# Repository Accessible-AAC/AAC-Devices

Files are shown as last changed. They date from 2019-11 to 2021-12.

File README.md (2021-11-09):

# AAC-Devices

Augmentative and alternative communications device design files based on inexpensive and open source technologies.

Printed circuit boards were designed using KiCAD (https://www.kicad.org/)

Enclosures were designed using OpenSCAD version 2015.03-2 (https://www.openscad.org/).

Solutions are designed around commodity electronic devices that should be inexpensive and readily available on-line.

<br />
This work is licensed under a <a rel="license" href="http://creativecommons.org/licenses/by-sa/4.0/">
Creative Commons Attribution-ShareAlike 4.0 International License</a>.

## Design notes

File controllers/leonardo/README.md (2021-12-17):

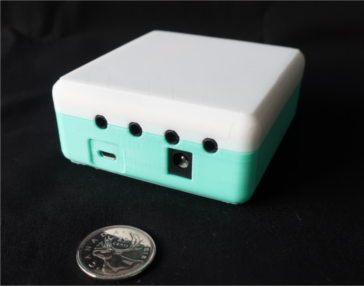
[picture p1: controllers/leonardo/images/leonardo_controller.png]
 

# Arduino Leonardo Controller

CAD files and firmware for a controller based on an Arduino leonardo board (https://store.arduino.cc/usa/leonardo) and a custom daughter board. 

## Leonardo Firmware

The most recent firmware for the controller can be found here: https://github.com/AbilitySpectrum/netCle/tree/master/Arduino/HubV1
(Please note that the firmware has been deprecated and is no longer actively supported.)

## Daughter Board Design Files

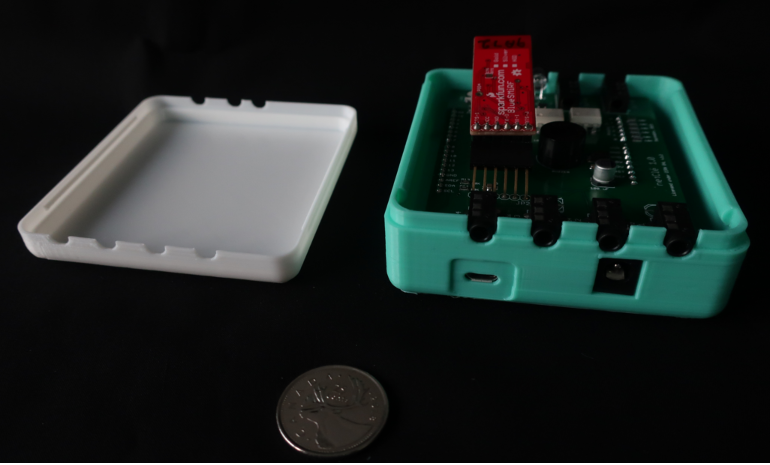
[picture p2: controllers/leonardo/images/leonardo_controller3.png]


The design for the daughter board can be found here: https://github.com/AbilitySpectrum/Sensact/tree/master/Board/v4.2

<br />This work is licensed under a <a rel="license" href="http://creativecommons.org/licenses/by-sa/4.0/">Creative Commons Attribution-ShareAlike 4.0 International License</a>.

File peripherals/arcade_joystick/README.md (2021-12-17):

# Arcade Joystick

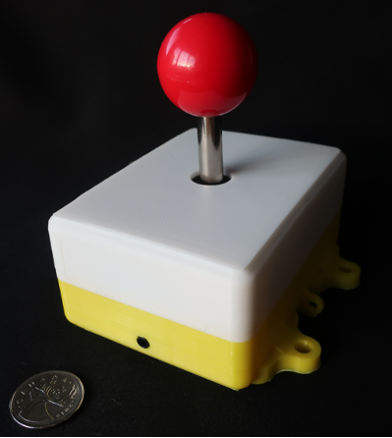
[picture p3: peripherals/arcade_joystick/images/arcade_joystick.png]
Arcade Joystick

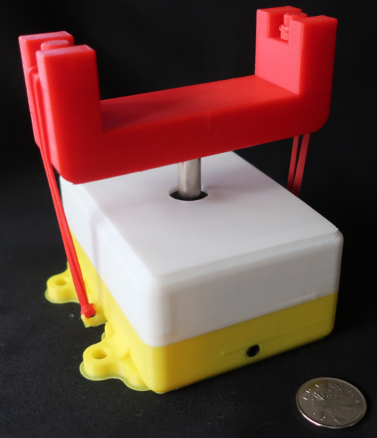
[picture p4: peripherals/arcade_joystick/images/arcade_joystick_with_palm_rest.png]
Arcade Joystick With Palm Rest


These directories contain design files for an arcade joystick peripheral.
 
This sensor can be plugged into an analog (yellow) controller input. It is activated by moving the handle.

## Assembly

Internal hardware mechanism is an arcade style 4/8 way joystick purchased from China.

It is held in place by four 8-32 x 1½" machine screws inserted into 4 embedded 8-32 nuts.

The joystick is connected to the interface PCB using hook-up wire:

    80 mm twisted pair soldered to D+, D-
    80 mm twisted pair soldered to R+, R-
    130 mm twisted pair soldered to L+, L-
    130 mm twisted pair soldered to U+, U-

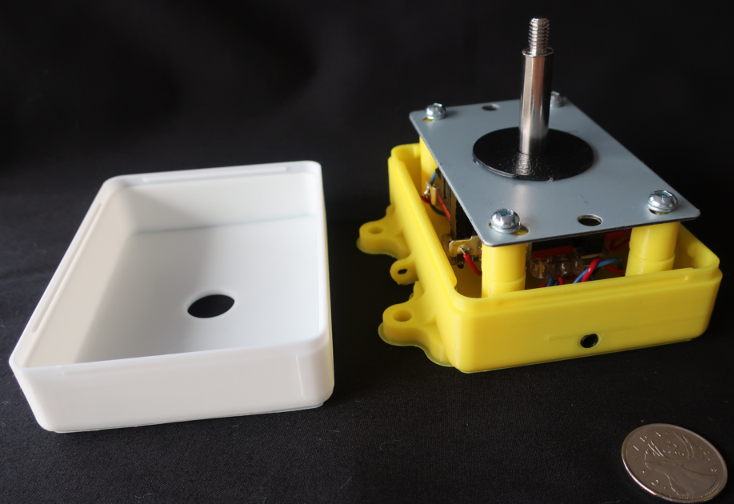
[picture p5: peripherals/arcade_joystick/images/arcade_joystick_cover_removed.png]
Arcade Joystick Enclosure with Cover removed


## Handles

The threads on the joystick handle are compatible with an M6 nut.

<a rel="license" href="http://creativecommons.org/licenses/by-sa/4.0/">

</a><br />This work is licensed under a <a rel="license" href="http://creativecommons.org/licenses/by-sa/4.0/">
Creative Commons Attribution-ShareAlike 4.0 International License</a>.

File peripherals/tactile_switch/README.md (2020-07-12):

# Tactile Switch

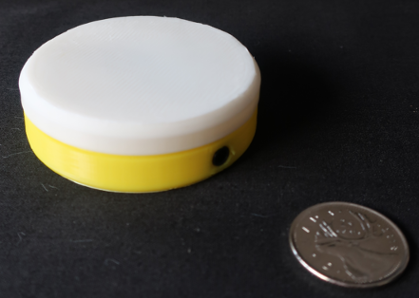
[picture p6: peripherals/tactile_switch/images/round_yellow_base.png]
Yellow Base Tactile Switch


These directories contain design files for a tactile switch peripheral.

When pressed, tactile switches with a yellow base connect the "Tip" on the TRRS connector to "Ring 1" and
can be connected directly into an analog (yellow) controller input. 

## Assembly

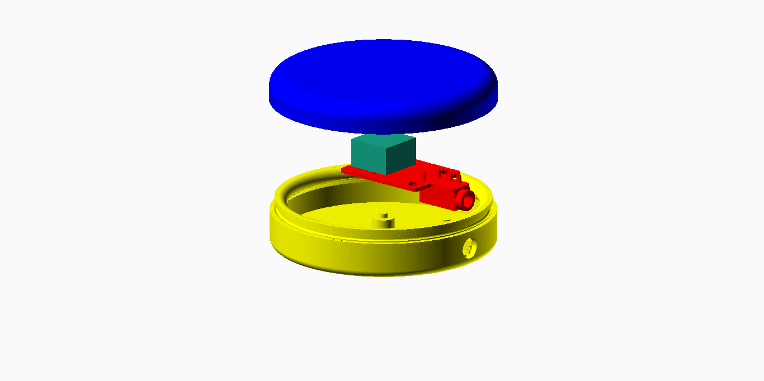
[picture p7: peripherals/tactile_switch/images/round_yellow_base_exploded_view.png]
Exploded View


## Parts

1 x 3.5mm Female Audio Connector 4 Pin DIP Stereo Headphone Jack PJ-320A

1 x 12mm x 12mm Tactile Switch

1 x tactile_switch_pcb_v2

1 x Round 59mm Button Enclosure

The PJ320A audio connector and the 12mm x 12mm tactile switch are available from various sources, including https://www.ebay.com/ and https://www.aliexpress.com/

<a rel="license" href="http://creativecommons.org/licenses/by-sa/4.0/">
</a>
<br />This work is licensed under a <a rel="license" href="http://creativecommons.org/licenses/by-sa/4.0/">
Creative Commons Attribution-ShareAlike 4.0 International License</a>.

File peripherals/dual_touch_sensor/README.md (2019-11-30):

# Dual Catalex Touch Sensor

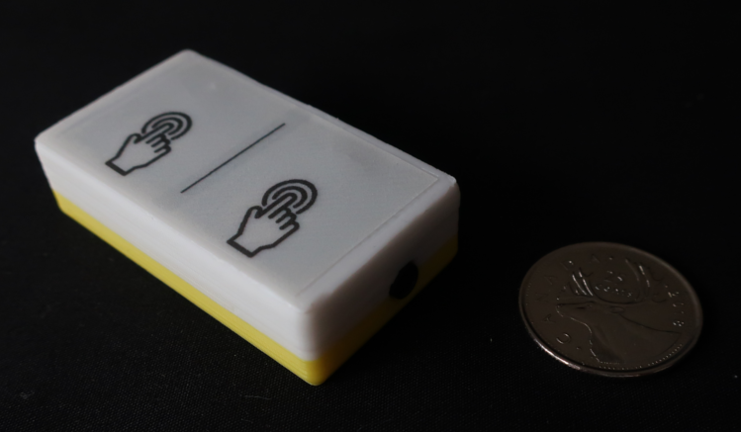
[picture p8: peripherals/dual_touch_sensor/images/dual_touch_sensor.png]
Dual Catalex Touch Sensor


These directories contain design files for a dual catalex touch sensor peripheral.

This sensor can be plugged into an analog (yellow) controller input. It is activated by touching the top, where indicated.

## Assembly

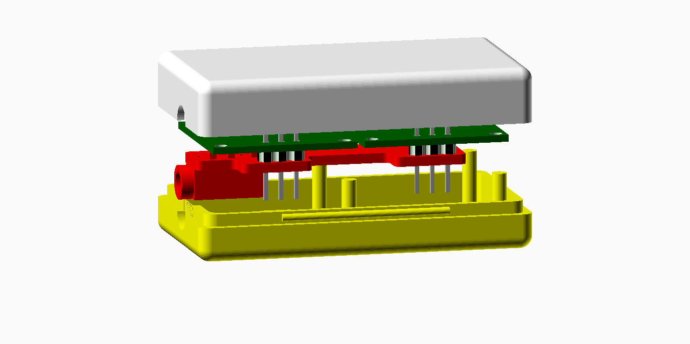
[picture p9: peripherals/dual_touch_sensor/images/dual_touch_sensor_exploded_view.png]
Exploded View


Catalex touch sensors should be tested before assembly to ensure that they will function correctly through the enclosure.

<a rel="license" href="http://creativecommons.org/licenses/by-sa/4.0/">

</a><br />This work is licensed under a <a rel="license" href="http://creativecommons.org/licenses/by-sa/4.0/">
Creative Commons Attribution-ShareAlike 4.0 International License</a>.

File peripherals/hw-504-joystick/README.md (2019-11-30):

# HW-504 Joystick

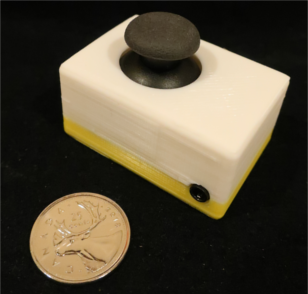
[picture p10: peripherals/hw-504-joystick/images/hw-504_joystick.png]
HW-504 Joystick


These directories contain design files for an HW-504 joystick peripheral.

This sensor can be plugged into an analog (yellow) controller input. It is activated by moving the black knob.

## Assembly

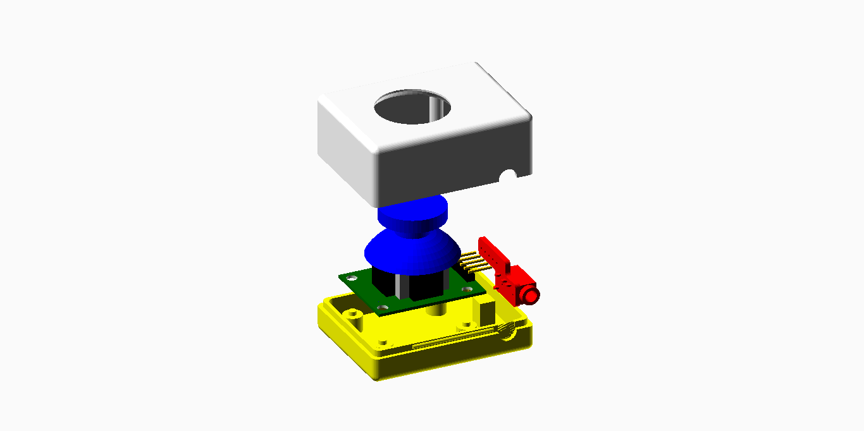
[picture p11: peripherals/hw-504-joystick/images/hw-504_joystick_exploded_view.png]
Exploded View


<a rel="license" href="http://creativecommons.org/licenses/by-sa/4.0/">

</a><br />This work is licensed under a <a rel="license" href="http://creativecommons.org/licenses/by-sa/4.0/">
Creative Commons Attribution-ShareAlike 4.0 International License</a>.

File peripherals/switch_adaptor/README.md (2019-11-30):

# Switch Adaptor

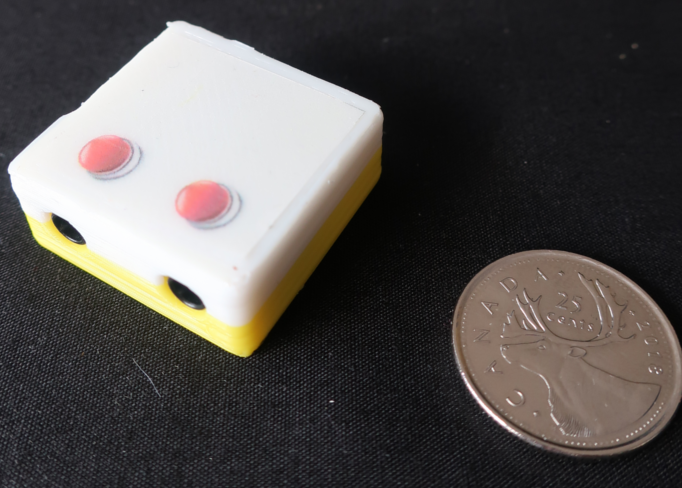
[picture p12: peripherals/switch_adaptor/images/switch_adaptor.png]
Switch Adaptor


These directories contain design files for a switch adaptor.

The switch adaptor is __required to connect a commercial switch (or a tactile switch
with a black base)__ to an analog (yellow) controller input. 

Switches should be plugged into the switch adaptor inputs indicated with the "red button icons".
The output connector (no icon) should be connected an analog (yellow) controller input.

__Failure to use a switch adaptor with these types of switches will result in the power being shorted
to the ground when the switch is pressed, possibly damaging the controller unit.__

## Assembly

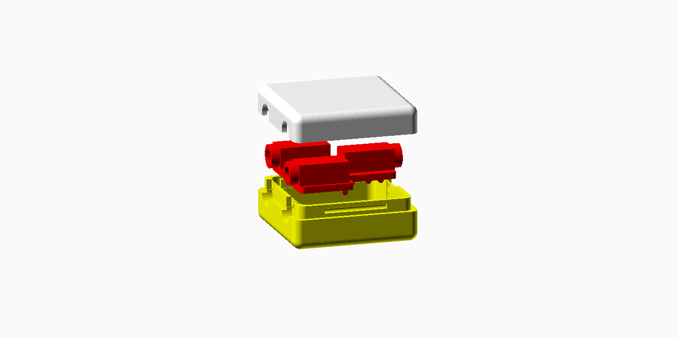
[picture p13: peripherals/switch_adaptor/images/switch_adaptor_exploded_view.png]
Exploded View


<a rel="license" href="http://creativecommons.org/licenses/by-sa/4.0/">
</a><br />
This work is licensed under a <a rel="license" href="http://creativecommons.org/licenses/by-sa/4.0/">
Creative Commons Attribution-ShareAlike 4.0 International License</a>.

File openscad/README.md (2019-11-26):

# OpenSCAD Common Files

The files in this directory are common files used to design various enclosures in this repository.

Files were created using OpenSCAD version 2015.03-2 (https://www.openscad.org/).

<br />This work is licensed under a <a rel="license" href="http://creativecommons.org/licenses/by-sa/4.0/">Creative Commons Attribution-ShareAlike 4.0 International License</a>.

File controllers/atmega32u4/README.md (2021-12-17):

# ATmega32U4 AAC Controller

These directories contain design files for two versions of an AAC controller based on the Atmel ATmega32U4.
The designs are functionally identical but use microcrontrollers in different form factors. 
Version 1.2 is based on an ATmega32U4-AU (44-TQFP) while version 1.3 is based on an ATmega32U4-MU (44-VQFNA).

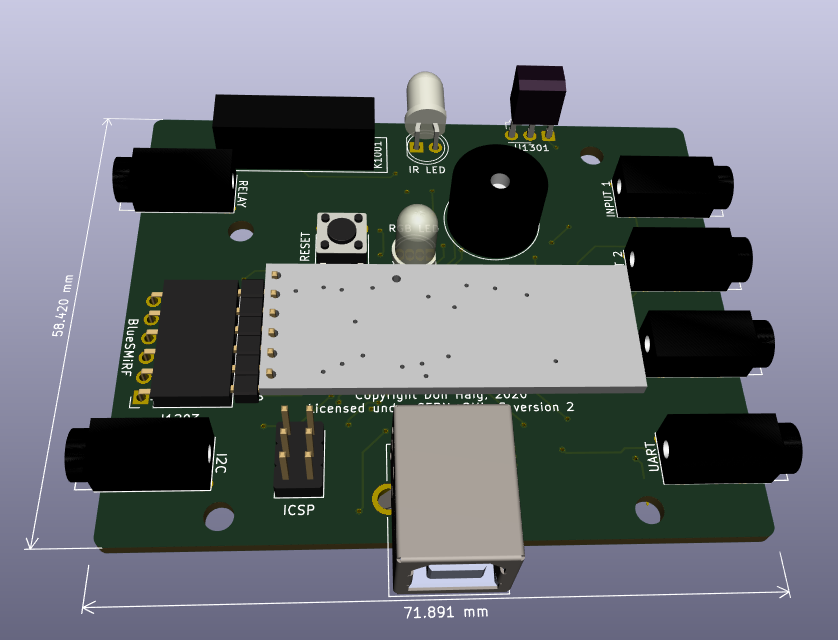
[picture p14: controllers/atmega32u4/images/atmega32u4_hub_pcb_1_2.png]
3D Rendering


## Firmware

The most recent firmware for the controller can be found here: https://github.com/AbilitySpectrum/netCle/tree/master/Arduino/HubV2

## netClé

This controller design is used in netClé™, distributed by the Tetra Society of North America: https://tetrasociety.org/netcle/

### Configuration 

Once programmed, the controller can be configured using: https://ncconfig.github.io/public_html/index.html

<br />This documentation is licensed under a <a rel="license" href="http://creativecommons.org/licenses/by-sa/4.0/">Creative Commons Attribution-ShareAlike 4.0 International License</a>.

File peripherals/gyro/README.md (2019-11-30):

# MPU-6050 Gyroscope/Accelerometer

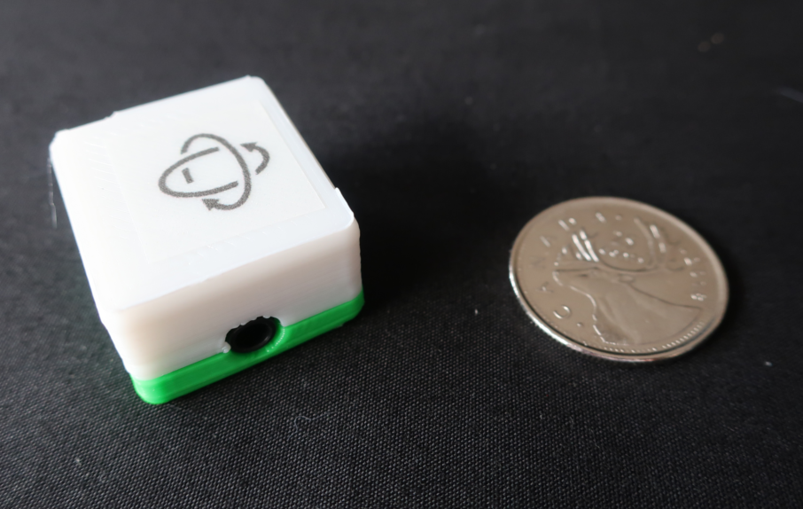
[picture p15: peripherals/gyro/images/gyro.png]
Gyroscope/Accelerometer


These directories contain design files for a gyroscope + accelerometer peripheral, for use with an
i2c (green) controller input.

## Hardware

The gyroscope/accelerometer peripheral is base on an MPU-6050 sensor:
<a rel="datasheet" href="https://www.invensense.com/wp-content/uploads/2015/02/MPU-6000-Datasheet1.pdf"> Datasheet</a>

I2C Address: 0x68

## Assembly

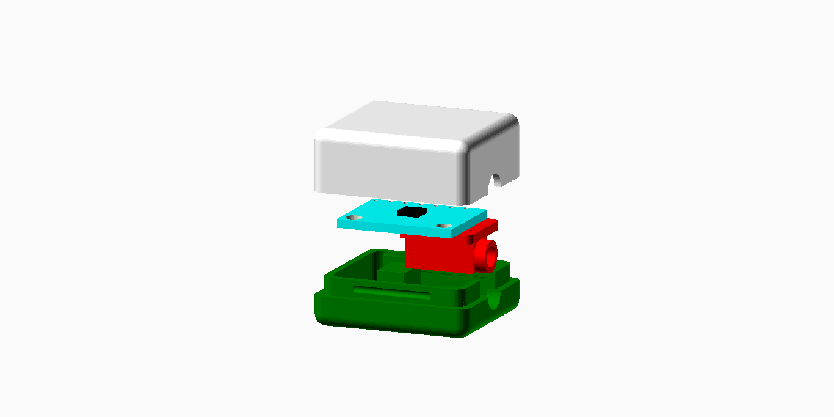
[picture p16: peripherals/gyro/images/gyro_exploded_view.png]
Exploded View


<a rel="license" href="http://creativecommons.org/licenses/by-sa/4.0/">

</a><br />This work is licensed under a <a rel="license" href="http://creativecommons.org/licenses/by-sa/4.0/">
Creative Commons Attribution-ShareAlike 4.0 International License</a>.

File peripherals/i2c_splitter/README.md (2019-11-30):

# I2C Splitter

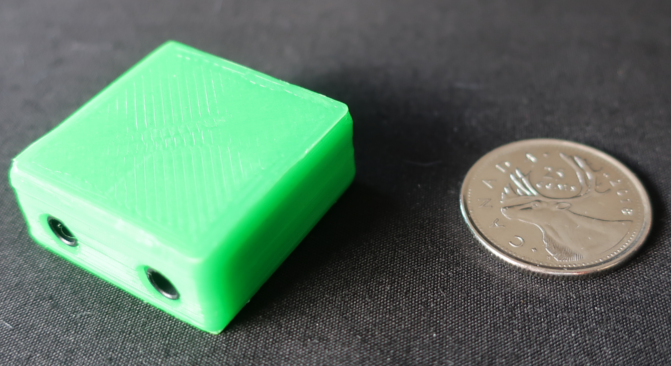
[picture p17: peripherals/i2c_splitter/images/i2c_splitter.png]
I2C Splitter


These directories contain design files for an i2c bus splitter, for use with an i2c (green) controller input.

This splitter can be used to connect two i2c (green base) peripherals to the same i2c (green) input port.

(Multiple splitters can be daisy-chained together to accommodate more i2c peripherals, subject to i2c bus limitation
with respect to peripheral addressing.)

## Assembly                                                                                                                                       

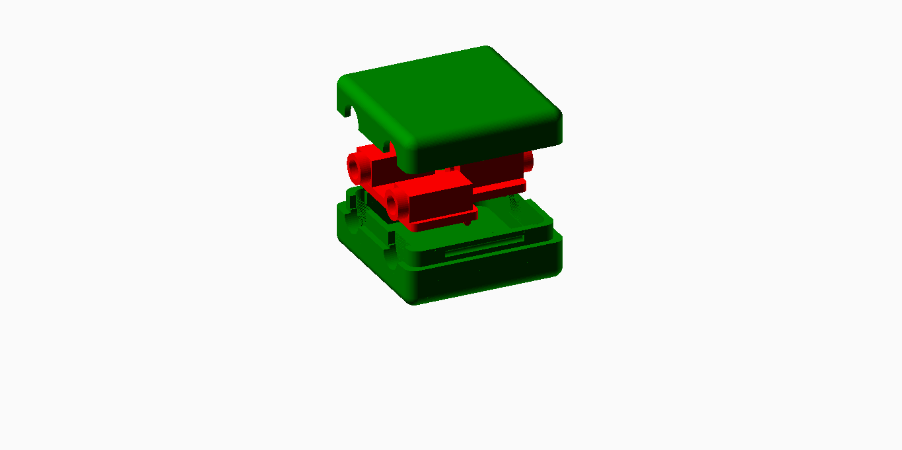
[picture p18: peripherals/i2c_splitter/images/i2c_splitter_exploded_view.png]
Exploded View
  

<a rel="license" href="http://creativecommons.org/licenses/by-sa/4.0/">

</a><br />This work is licensed under a <a rel="license" href="http://creativecommons.org/licenses/by-sa/4.0/">
Creative Commons Attribution-ShareAlike 4.0 International License</a>.

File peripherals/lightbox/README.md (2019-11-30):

# Lightbox Display

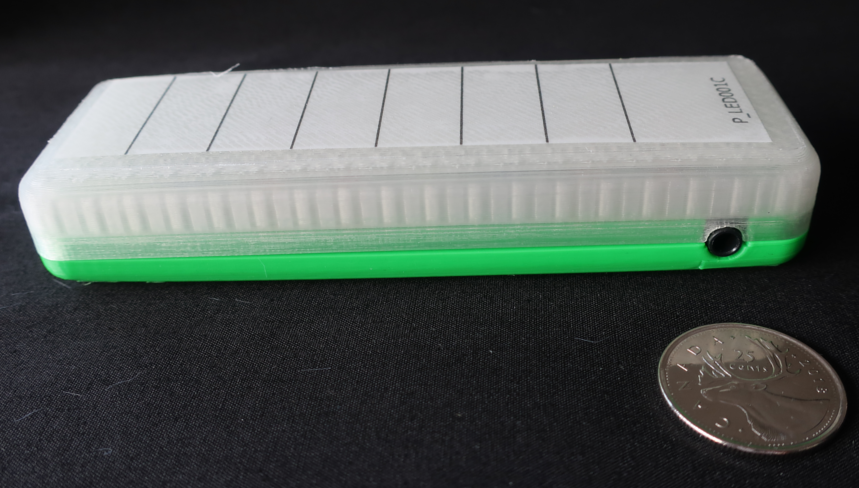
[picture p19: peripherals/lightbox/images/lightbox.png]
Lightbox Display


These directories contain design files for a lightbox display peripheral, for use with an i2c (green) controller input.

## Hardware

The lightbox is based on a Microchip MCP23008 8-Bit I/O Expander: <a rel="datasheet" 
href="https://ww1.microchip.com/downloads/en/DeviceDoc/21919e.pdf">Datasheet</a>

I2C Address: 0x20

## Assembly

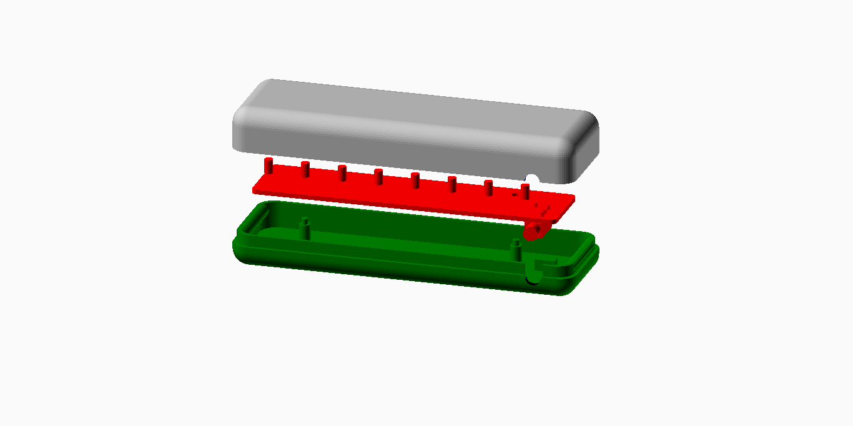
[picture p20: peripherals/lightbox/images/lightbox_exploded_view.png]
Exploded View


<a rel="license" href="http://creativecommons.org/licenses/by-sa/4.0/">

</a><br />This work is licensed under a <a rel="license" href="http://creativecommons.org/licenses/by-sa/4.0/">
Creative Commons Attribution-ShareAlike 4.0 International License</a>.

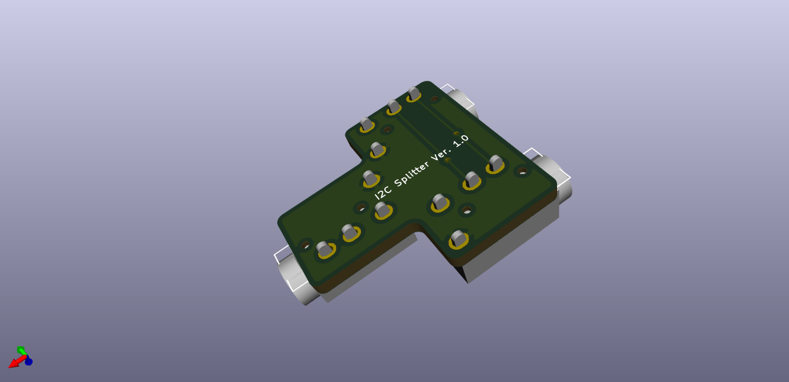
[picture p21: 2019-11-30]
peripherals/i2c_splitter/images/i2c_splitter_pcb.png

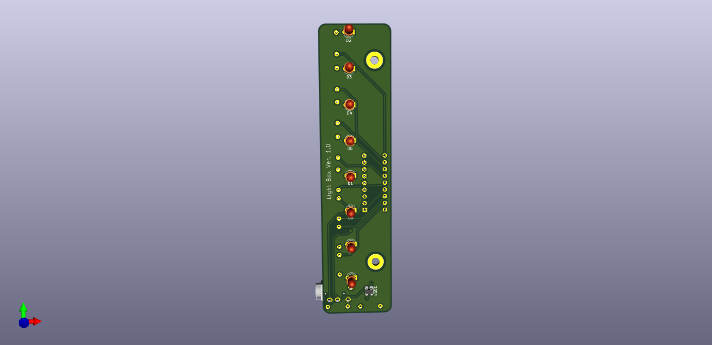
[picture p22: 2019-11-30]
peripherals/lightbox/images/lightbox_pcb_2.png

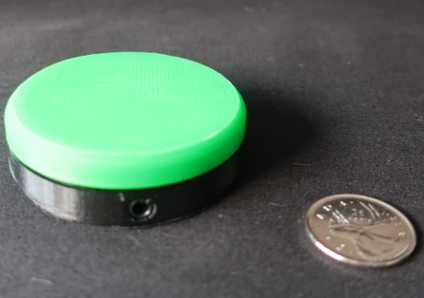
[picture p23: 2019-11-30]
peripherals/tactile_switch/images/round_black_base.png

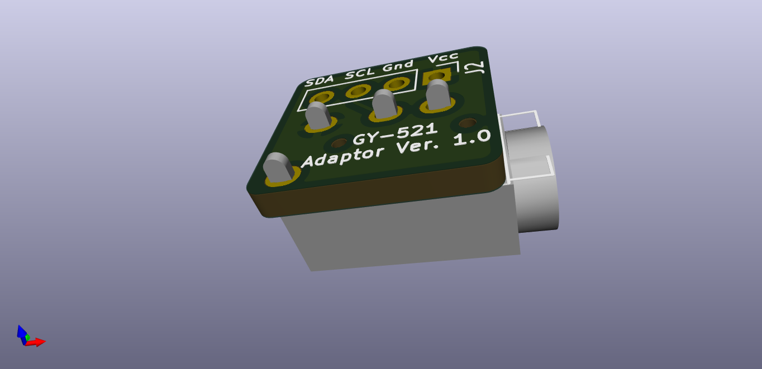
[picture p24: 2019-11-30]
peripherals/gyro/images/gy-521_trrs_pcb.png

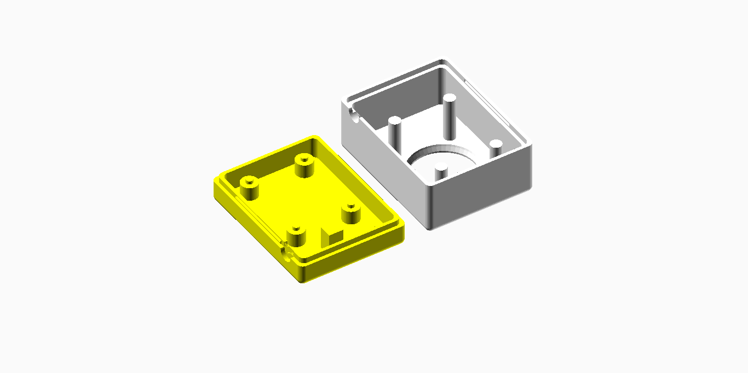
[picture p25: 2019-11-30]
peripherals/hw-504-joystick/images/hw-504_joystick_enclosure.png

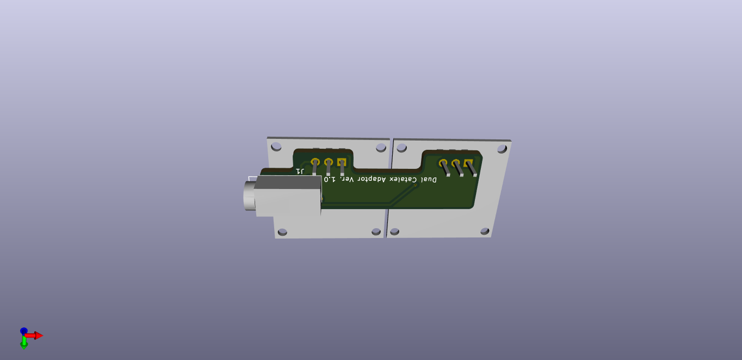
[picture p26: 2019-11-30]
peripherals/dual_touch_sensor/images/dual_touch_sensor_trrs_pcb.png

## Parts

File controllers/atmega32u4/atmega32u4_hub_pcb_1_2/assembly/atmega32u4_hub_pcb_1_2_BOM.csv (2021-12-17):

Comment | Designator | Footprint | LCSC
12mm_Buzzer | Buzzer701 |  |  | https://www.aliexpress.com/item/4000133619336.html?spm=a2g0s.9042311.0.0.27424c4dESjgPi
22uF | C101,C102,C103,C107,C108,C110,C111 | 805 | C45783 | https://lcsc.com/product-detail/Multilayer-Ceramic-Capacitors-MLCC-SMD-SMT_Samsung-Electro-Mechanics-CL21A226MAQNNNE_C45783.html
1uF | C104 | 805 | C28323 | https://lcsc.com/product-detail/Multilayer-Ceramic-Capacitors-MLCC-SMD-SMT_Samsung-Electro-Mechanics-CL21B105KBFNNNE_C28323.html
20pF | C105,C109 | 603 | C1648 | https://lcsc.com/product-detail/Multilayer-Ceramic-Capacitors-MLCC-SMD-SMT_Samsung-Electro-Mechanics-CL10C200JB8NNNC_C1648.html
100nF | C106 | 805 | C49678 | https://lcsc.com/product-detail/Multilayer-Ceramic-Capacitors-MLCC-SMD-SMT_YAGEO-CC0805KRX7R9BB104_C49678.html
10uF | C1101 | 805 | C15850 | https://lcsc.com/product-detail/Multilayer-Ceramic-Capacitors-MLCC-SMD-SMT_Samsung-Electro-Mechanics-CL21A106KAYNNNE_C15850.html
1N4007 | D1001 | SMA,DO-214AC | C95872 | https://lcsc.com/product-detail/Diodes-General-Purpose_MDD-Microdiode-Electronics-M7_C95872.html
RX | D101 | 603 | C72043 | https://lcsc.com/product-detail/Light-Emitting-Diodes-LED_Everlight-Elec-19-217-GHC-YR1S2-3T_C72043.html
RGB LED | D102 |  |  | https://www.aliexpress.com/item/1656753326.html?spm=a2g0s.9042311.0.0.27424c4dJetW7l
TX | D103 | 603 | C72044 | https://lcsc.com/product-detail/Light-Emitting-Diodes-LED_0603-Red-LED_C72044.html
L | D104 | 603 | C72038 | https://lcsc.com/product-detail/Light-Emitting-Diodes-LED_Everlight-Elec-19-213-Y2C-CQ2R2L-3T-CY_C72038.html
IR LED | D701
ESDA5V3L | ESD201,ESD301,ESD401,ESD501,ESD1101,ESD1201,ESD1202 | SOT-23-3 | C87911 | https://lcsc.com/product-detail/TVS_STMicroelectronics-ESDA5V3L_C87911.html
TLC-FSMD050 | F1201 | 603 | C261937 | https://lcsc.com/product-detail/PTC-Resettable-Fuses_TLC-Electronic-TLC-FSMD050_C261937.html
Conn_02x03_Odd_Even | J101 | PinHeader_2x03_P2.54mm_Vertical | C225518 | https://lcsc.com/product-detail/Pin-Header-Female-Header_CJT-Changjiang-Connectors-A2541WV-2x3P_C225518.html
USB_B | J1201 |  | C498173 | https://lcsc.com/product-detail/New-Arrivals_SOFNG-USB-B01_C498173.html
BlueSMiRF | J1203 |  | C225514 | https://lcsc.com/product-detail/Pin-Header-Female-Header_CJT-Changjiang-Connectors-A2541HWR-6P_C225514.html
PJ320A | J201,J301,J401,J501,J1001,J1202 |  |  | https://www.aliexpress.com/item/32775943831.html?spm=a2g0s.9042311.0.0.27424c4dvTAhw2
RELAY | K1001 |  | C10496 | https://lcsc.com/product-detail/Relays_PAN-CHANG-SIP-1A05_C10496.html
BSS138 | Q701,Q801,Q901 | SOT-23-3 | C82045 | https://lcsc.com/product-detail/MOSFET_ON-Semiconductor-BSS138LT1G_C82045.html
10k | R104,R101,R102,R103,R105,R108,R115,R116,R201,R202,R801,R802 | 603 | C25804 | https://lcsc.com/product-detail/Chip-Resistor-Surface-Mount_UNI-ROYAL-Uniroyal-Elec-0603WAF1002T5E_C25804.html
1k | R111,R113,R114 | 603 | C21190 | https://lcsc.com/product-detail/Chip-Resistor-Surface-Mount_UNI-ROYAL-Uniroyal-Elec-0603WAF1001T5E_C21190.html
330 | R112,R106,R107 | 603 | C23138 | https://lcsc.com/product-detail/Chip-Resistor-Surface-Mount_UNI-ROYAL-Uniroyal-Elec-0603WAF3300T5E_C23138.html
22 | R1202,R1201 | 603 | C23345 | https://lcsc.com/product-detail/Chip-Resistor-Surface-Mount_UNI-ROYAL-Uniroyal-Elec-0603WAF220JT5E_C23345.html
47 | R701 | 1206 | C25384 | https://lcsc.com/product-detail/Chip-Resistor-Surface-Mount_UNI-ROYAL-Uniroyal-Elec-1206W4J0470T5E_C25384.html
RESET | SW101 | 6mm x 6mm | C455095 | https://lcsc.com/product-detail/Tactile-Switches_XUNPU-TS-1002-07026_C455095.html
ATmega32U4-AU | U101 | QFP-44_10.0x10.0x0.8P | C44854 | https://lcsc.com/product-detail/ATMEL-AVR_ATMEL_ATMEGA32U4-AU_ATMEGA32U4-AU_C44854.html
TSOP38238 | U1301
16 MHz | Y101 | SMD-3225_4P | C13738 | https://lcsc.com/product-detail/SMD-Crystal-Resonators_Yangxing-Tech-X322516MLB4SI_C13738.html

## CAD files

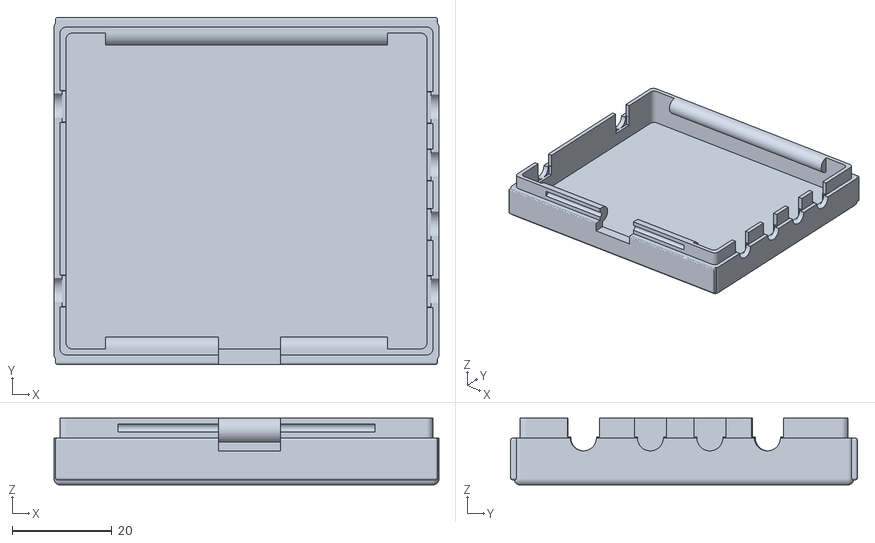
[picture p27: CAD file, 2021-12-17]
controllers/atmega32u4/enclosure/v1.2.2/stl_files/bottom.stl
77.0 x 69.4 x 13.4

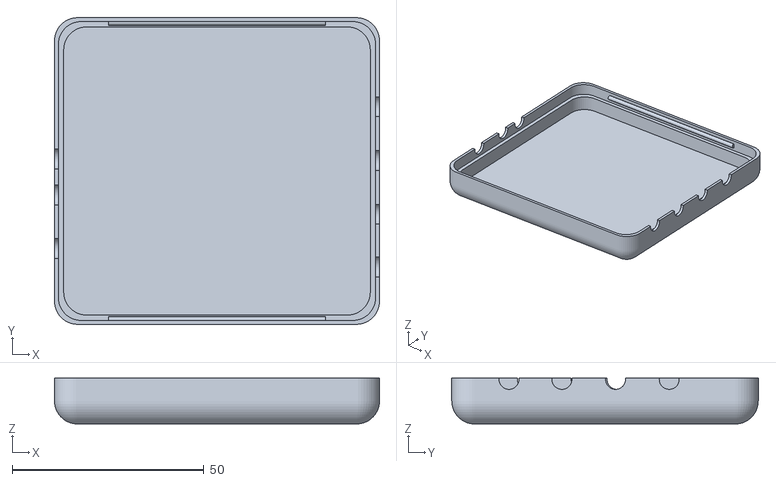
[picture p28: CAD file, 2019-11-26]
controllers/leonardo/enclosure/stl_files/v2/enclosure_top_v2.stl
84.8 x 80.0 x 12.0

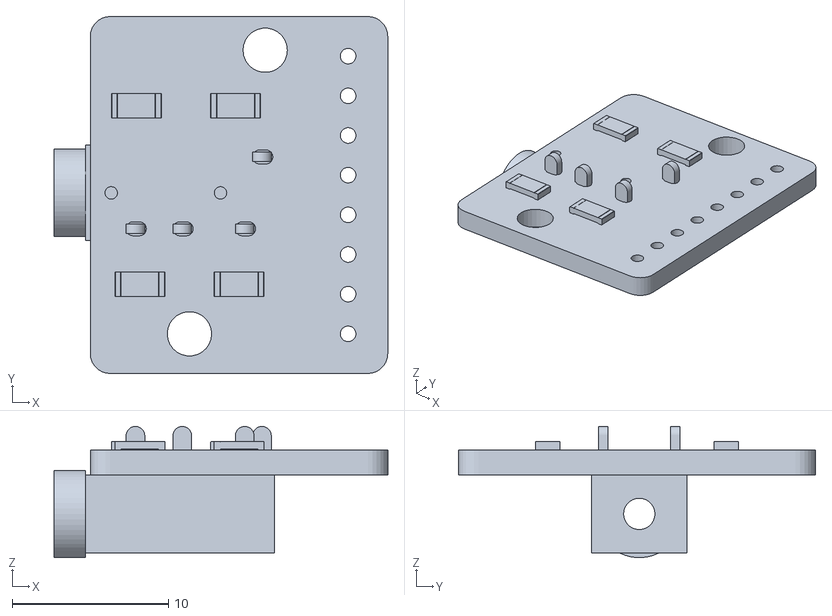
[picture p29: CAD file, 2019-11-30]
peripherals/arcade_joystick/enclosure/v3/interface_pcb.stl
21.4 x 22.9 x 8.39

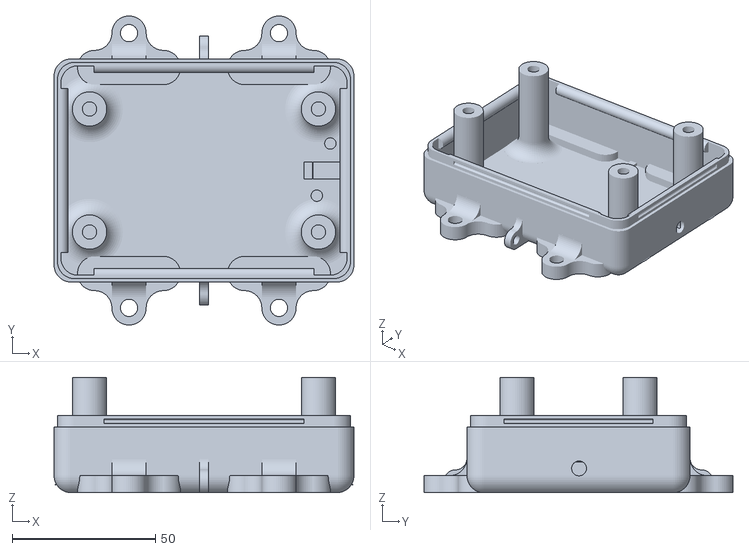
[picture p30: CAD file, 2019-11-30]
peripherals/arcade_joystick/enclosure/v3/stl_files/arcade_joystick_bottom.stl
104.8 x 108.0 x 40.4

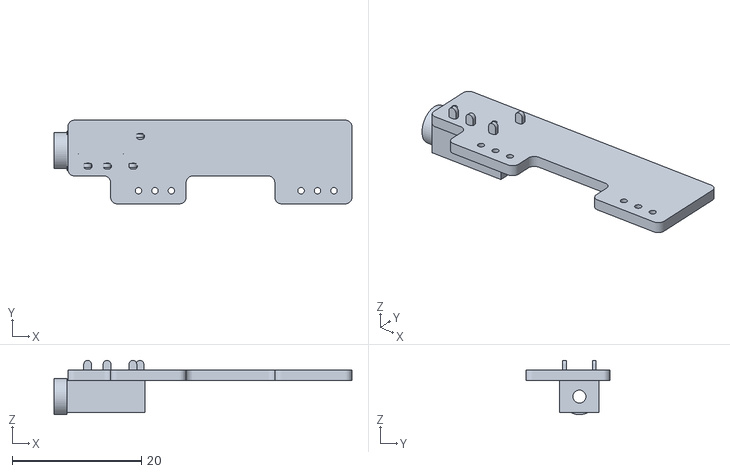
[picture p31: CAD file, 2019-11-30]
peripherals/dual_touch_sensor/enclosure/v2/dual_touch_sensor_pcb.stl
46.1 x 13.0 x 8.39

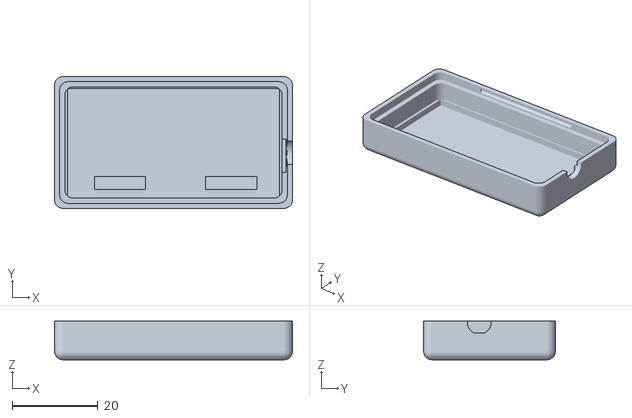
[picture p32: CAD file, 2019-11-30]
peripherals/dual_touch_sensor/enclosure/v2/stl_files/dual_touch_sensor_enclosure_top.stl
55.6 x 30.8 x 9.00

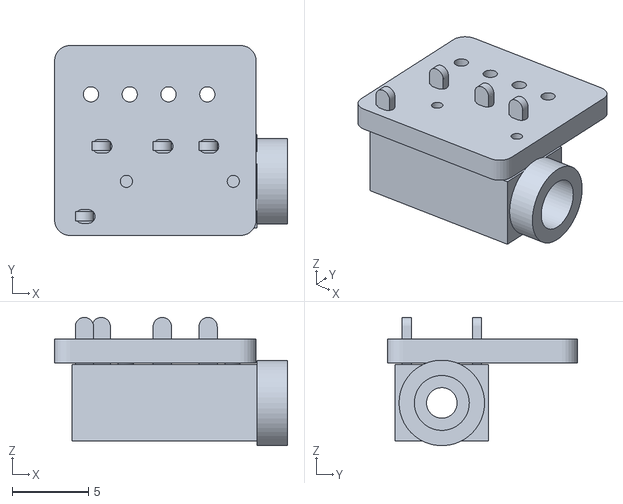
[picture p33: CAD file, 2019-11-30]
peripherals/gyro/enclosure/v2/gy-521_pcb.stl
15.3 x 12.4 x 8.39

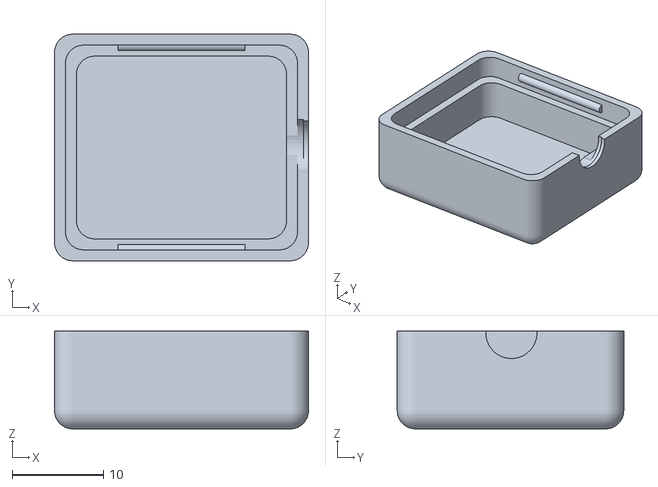
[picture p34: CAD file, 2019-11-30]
peripherals/gyro/enclosure/v2/stl_files/gy-521_sensor_enclosure_top.stl
27.8 x 24.8 x 10.7

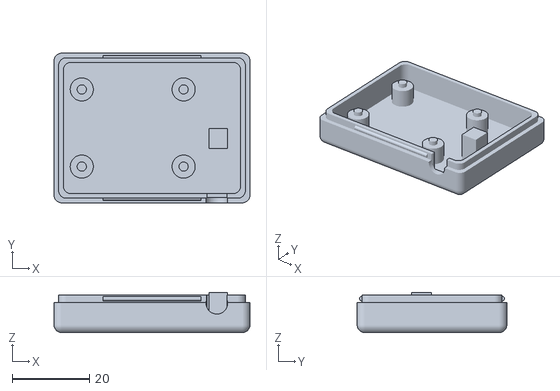
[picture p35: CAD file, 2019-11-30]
peripherals/hw-504-joystick/enclosure/v2/stl_files/joystick_enclosure_bottom.stl
50.8 x 38.8 x 10.4

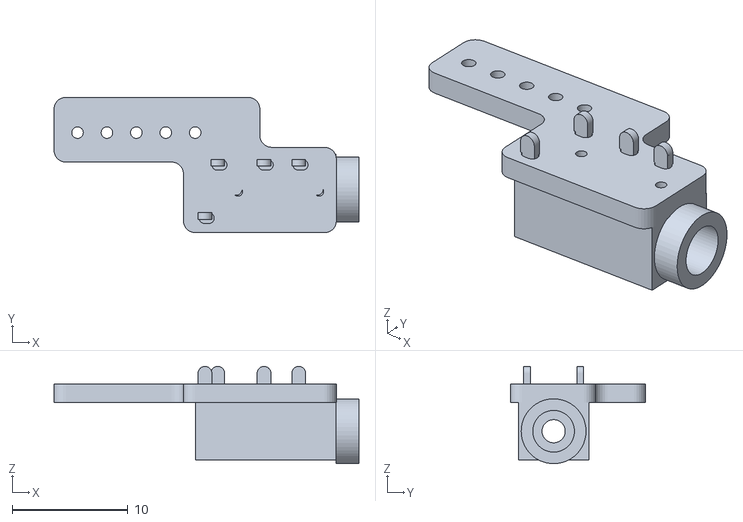
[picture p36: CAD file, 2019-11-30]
peripherals/hw-504-joystick/enclosure/v2/trrs_pcb.stl
26.3 x 11.7 x 8.39

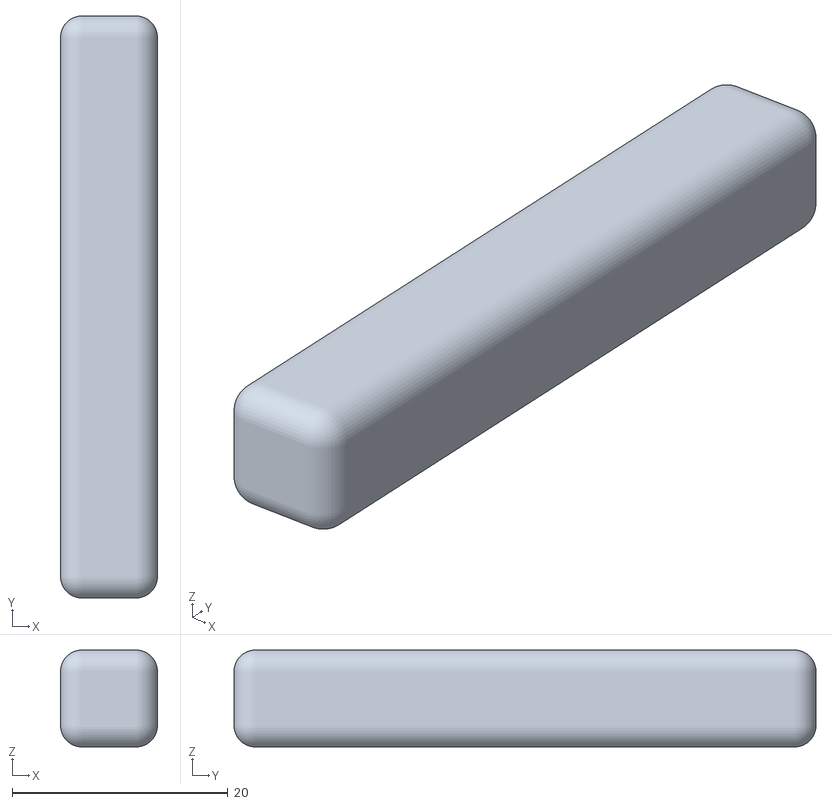
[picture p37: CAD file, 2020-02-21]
peripherals/hw-504-joystick/handle/stl_files/hw-504_handle.stl
9.00 x 54.0 x 8.99

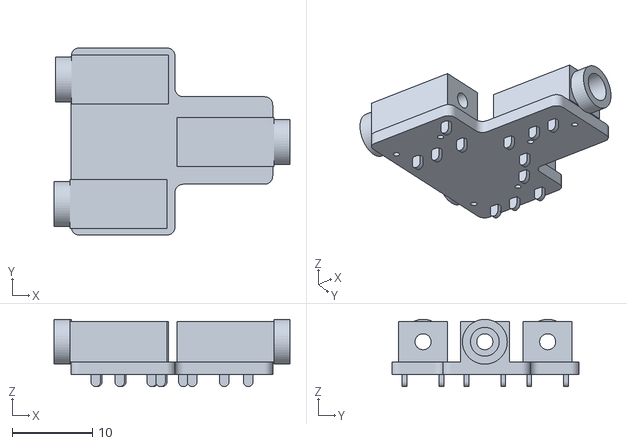
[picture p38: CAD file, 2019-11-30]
peripherals/i2c_splitter/enclosure/i2c_splitter_pcb.stl
29.4 x 23.4 x 8.39

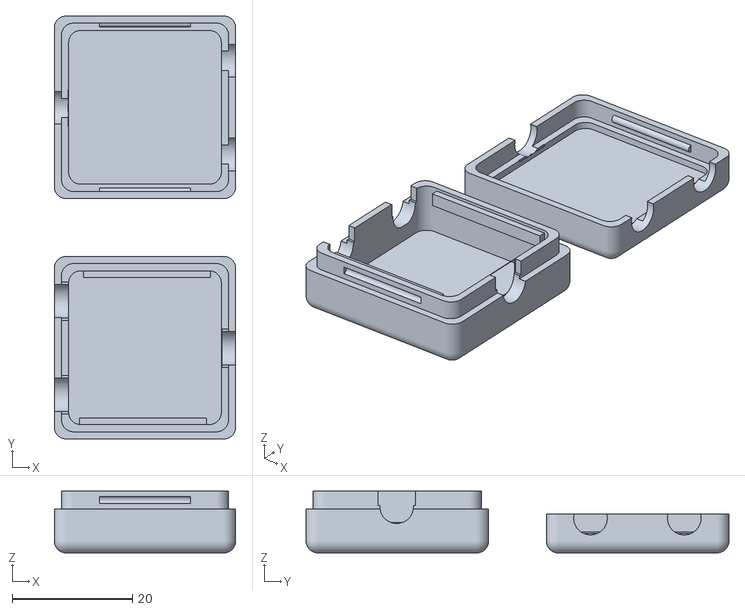
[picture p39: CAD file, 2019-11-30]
peripherals/i2c_splitter/enclosure/stl_files/switch_adaptor_enclosure.stl
30.2 x 70.4 x 10.3

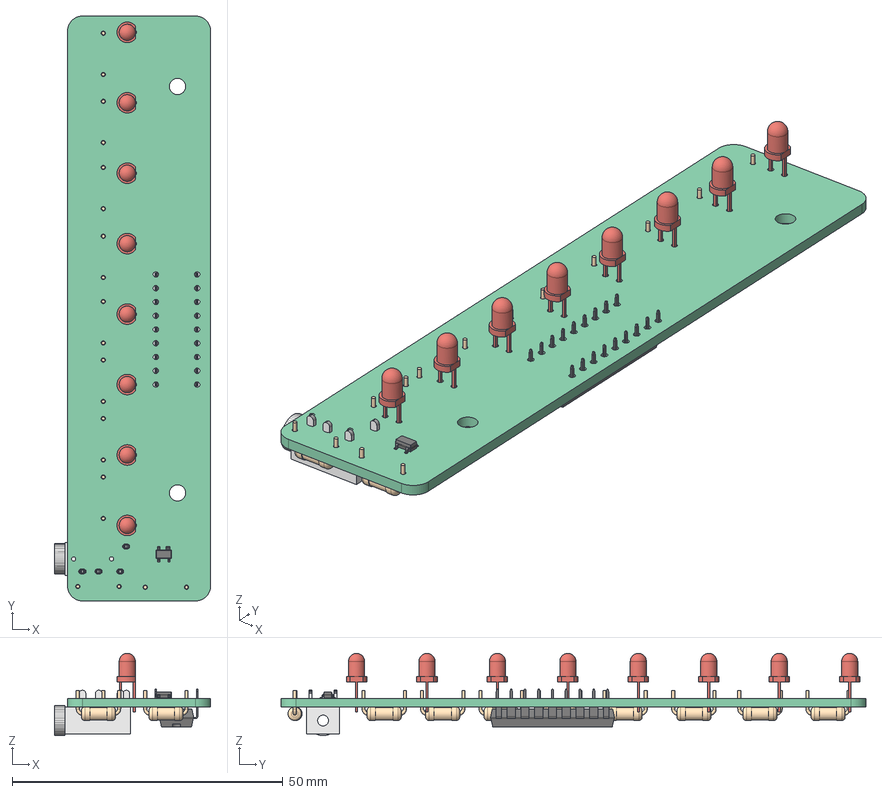
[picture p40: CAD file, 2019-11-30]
peripherals/lightbox/enclosure/v3/lightbox_pcb_v3.FCStd
28.8 x 108.0 x 15.2 mm
Pcb
ESD1_SOT_143_5CF6B7F7
D8_LED_D3.0mm_5CF71A60
D7_LED_D3.0mm_5CF6479C
D6_LED_D3.0mm_5CF647D2
D5_LED_D3.0mm_5CF64808
D4_LED_D3.0mm_5CF646B8
D3_LED_D3.0mm_5CF646EE
D2_LED_D3.0mm_5CF71B3B
D1_LED_D3.0mm_5CF64874
U1_DIP-18_W7.62mm_5CF635C0
R10_R_Axial_DIN0207_L63mm_D25mm_P762mm_Horizontal_5CF72305
R9_R_Axial_DIN0207_L63mm_D25mm_P762mm_Horizontal_5CF6BF18
R8_R_Axial_DIN0207_L63mm_D25mm_P762mm_Horizontal_5CF71A1C
R7_R_Axial_DIN0207_L63mm_D25mm_P762mm_Horizontal_5CF644EE
R6_R_Axial_DIN0207_L63mm_D25mm_P762mm_Horizontal_5CF64530
R5_R_Axial_DIN0207_L63mm_D25mm_P762mm_Horizontal_5CF645B4
R4_R_Axial_DIN0207_L63mm_D25mm_P762mm_Horizontal_5CF645F6
R3_R_Axial_DIN0207_L63mm_D25mm_P762mm_Horizontal_5CF64638
R2_R_Axial_DIN0207_L63mm_D25mm_P762mm_Horizontal_5CF71AFD
R1_R_Axial_DIN0207_L63mm_D25mm_P762mm_Horizontal_5CF70D55
J1_connector_pj320a002_(Solid)_5CF722CF[2]

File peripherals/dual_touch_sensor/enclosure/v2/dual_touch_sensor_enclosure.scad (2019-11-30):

/* dual_touch_sensor_enclosure.scad
 *
 *    OpenSCAD script to generate an enclosure for dual catalex touch sensor board
 *
 *    Copyright 2018 Don Haig (time4tux at gmail dot com)
 *
 *    GNU GPLv3 (See LICENSE for details) 
 *
 */
$fn = 50;

use<catalex_pcb.scad>
use<pj320a.scad>
use<rounded_minkowski_box.scad>
use<straight_header.scad>

u_d_pcb = 1.9;  // up - down adjustment on z-axis for PCB


/* 3D printer parameters */                                                                                                                      
    nozzle_diam = 0.4;    // 3D printer nozzle diameter in mm                                                                                         
    layer_res = 0.1;      // 3D printer layer resolution in mm                                                                                              

/* Enclosure Dimensions */
    tol = 0.01;                // printing tolerance (should be evenly divisible by nozzle diameter)
    lip_w1 = 1.2;              // thickness of outer lip (should be evenly divisible by nozzle diameter)
    lip_w2 = 1.2;              // thickness of inner lip (should be evenly divisible by nozzle diameter)
    t = lip_w1+lip_w2;         // total wall thickness (should be evenly divisible by nozzle diameter)
    l = 50.8+2*t;              // Outside Length of enclosure (should be evenly divisible by nozzle diameter)
    w = 26 + 2*t;              // Outside width of enclosure (should be evenly divisible by nozzle diameter)
    h_t = 8.0;                   // height of top piece of enclosure (should be evenly divisible by layer resolution)
    h_b = 6.8;                  // height of bottom piece of enclosure (should be evenly divisible by layer resolution)
    r = 2;                     // Outside corner radius
    lip_h = 2;               // height of lip (should be evenly divisible by layer resolution)


    check_dimension(l, nozzle_diam);
    check_dimension(w, nozzle_diam);
    check_dimension(t, nozzle_diam);
    check_dimension(lip_w1, nozzle_diam);
    check_dimension(lip_w2, nozzle_diam);

    check_dimension(h_t, layer_res);
    check_dimension(h_b, layer_res);
    check_dimension(lip_h, layer_res);

module connector(cutout) {

      translate([26.5, 2.4, 6.1])
     rotate([0,180,90]) color("black") pj320a(cutout);
}

module cover () {
    l = 22.0;
    w = 22.0;
    h = 0.3;

    difference() {
        minkowski() {
            color("white") cube([l, w, h], center=true);
            cylinder(r=2, h=h, center = true);
        }

    //translate([0, 0, h/2]) substrate();
    translate([0, 0, -1]) header_pins_cutout();
    //translate([-15, -15, -3.5]) cube([30, 30, 4.5]);
    }
}

module top() {
    module cut_out() {
        l = 48.8;
        w = 24.8;
        h = 1.8;

        translate ([0, -3, 12])
        difference() {
            minkowski() {
                color("white") cube([l, w, h], center=true);
                cylinder(r=0.4, h=h, center = true);
            }
        }
    }

    difference() {
        translate([0, 0, h_t+2])
        rotate([0, 180, 0])
        rounded_minkowski_outer_lip(l, w, h_t, r, lip_w2, lip_h, t, tol);
        connector();
        // pcb cut-outs
        translate([12.8+11.5, -0.8, 0]) cube([2, 7.8, 8]); // side
        translate([-4+11.5, +8, 9.6]) cube([12, 3, 2.2]);  // top
        translate([-4-14.5, +8, 9.6]) cube([12, 3, 2.2]);  // top
        //cut_out();
        //translate([11.5, 0, -t]) guts();
        translate([0, 3.2, -2.2]) color("red")cut_out();
    }
//    translate([0, 0, -t]) guts();

}

module bottom() {
    difference() {
        rounded_minkowski_inner_lip(l, w, h_b, r, lip_w1, lip_h, t, tol);
        connector(cutout = "down");
        //translate([8, 8, 3.2]) rotate([0,90,90]) color("black") pj320a(cutout = true);
        //magnets();
    }
   // connector backstop
   //connector(cutout = "down");
   translate([-2.4+11.5, 0, 0]) cube([5, 7, 3]);

   // Sensor supports
   s_c = 10.2;  // support center
   s_h = 9.5;
   //translate([s_c,s_c, 0]) cylinder(r= 0.8, h=s_h+1);
   //translate([s_c,s_c, 0]) cylinder(r= 2.5, h=s_h);

   //translate([s_c,-s_c, 0]) cylinder(r= 0.8, h=s_h+1);
   //translate([s_c,-s_c, 0]) cylinder(r= 2.5, h=s_h);

   //translate([-s_c,s_c, 0]) cylinder(r= 0.8, h=s_h+1);
   translate([-s_c+12, s_c, 0]) cylinder(r= 1.2, h=s_h);
   translate([-s_c-13, s_c, 0]) cylinder(r= 1.2, h=s_h);

   //translate([-s_c,-s_c, 0]) cylinder(r= 0.8, h=s_h+1);
   translate([-s_c+12,-s_c, 0]) cylinder(r= 1.2, h=s_h);
   translate([-s_c-13,-s_c, 0]) cylinder(r= 1.2, h=s_h);
}

echo(str("Rounded Minkowski Box: ", l, "mm x ", w, "mm x ", h_t + h_b, "mm") );

module guts() {
    translate([1.35, 0.2, 9.5+t]) touch_sensor_pcb();
    translate([-23.8, 0.2, 9.5+t]) touch_sensor_pcb();
    translate([-11.8, -5.8, 7.5+t]) rotate([0, 0, 180]) color ("red") import("dual_touch_sensor_pcb.stl");
}

module enclosure () {
    //translate([0, 40, h_t+2*t]) rotate([0, 180, 180])
    translate([0, 0, 15])
    color("white")top();

    //translate([-40, 0, -0.9])
    //translate([0, 0, 11])
    //rotate([0, 180, 0])
    //cover();

    //translate([0, 0, t])
    color("yellow")bottom();

    translate([11.5, 0, 3])
    guts();

}

//difference() {
enclosure();
//translate([5, 5, 0]) cube([50, 50, 50]);
//}

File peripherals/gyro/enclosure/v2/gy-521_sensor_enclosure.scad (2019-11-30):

/* gy-521_sensor_enclosure.scad
 *
 *    OpenSCAD script to generate an enclosure for mpu-6050 accel/gyro sensor board
 *
 *    Copyright 2019 Don Haig (time4tux at gmail dot com)
 *
 *    GNU GPLv3 (See LICENSE for details) 
 *
 */
$fn = 50;

use<mpu-6050_pcb.scad>
use<pj320a.scad>
use<rounded_minkowski_box.scad>
use<straight_header.scad>

u_d_pcb = 1.9;  // up - down adjustment on z-axis for PCB


/* 3D printer parameters */                                                                                                                      
    nozzle_diam = 0.4;    // 3D printer nozzle diameter in mm                                                                                         
    layer_res = 0.1;      // 3D printer layer resolution in mm                                                                                              

/* Enclosure Dimensions */
    tol = 0.01;                // printing tolerance (should be evenly divisible by nozzle diameter)
    lip_w1 = 1.2;              // thickness of outer lip (should be evenly divisible by nozzle diameter)
    lip_w2 = 1.2;              // thickness of inner lip (should be evenly divisible by nozzle diameter)
    t = lip_w1+lip_w2;         // total wall thickness (should be evenly divisible by nozzle diameter)
    l = 23+2*t;              // Outside Length of enclosure (should be evenly divisible by nozzle diameter)
    w = 20 + 2*t;              // Outside width of enclosure (should be evenly divisible by nozzle diameter)
    h_t = 9.2;                   // height of top piece of enclosure (should be evenly divisible by layer resolution)
    h_b = 6.8;                  // height of bottom piece of enclosure (should be evenly divisible by layer resolution)
    r = 2;                     // Outside corner radius
    lip_h = 3;               // height of lip (should be evenly divisible by layer resolution)


    check_dimension(l, nozzle_diam);
    check_dimension(w, nozzle_diam);
    check_dimension(t, nozzle_diam);
    check_dimension(lip_w1, nozzle_diam);
    check_dimension(lip_w2, nozzle_diam);

    check_dimension(h_t, layer_res);
    check_dimension(h_b, layer_res);
    check_dimension(lip_h, layer_res);

    snaps = "reverse"; 

module connector(cutout) {

      translate([11.4, -0.1, 5.6])
     rotate([0,180,90]) color("black") pj320a(cutout);
}


module top() {
    module cut_out() {
        l = 22.6;
        w = 21.2;
        h = 1.8;

        translate ([0, -3, 12])
        difference() {
            minkowski() {
                color("white") cube([l, w, h], center=true);
                cylinder(r=2, h=h, center = true);
            }
        }
    }

    difference() {
        translate([0, 0, h_t+2])
        rotate([0, 180, 0])
        rounded_minkowski_outer_lip(l, w, h_t, r, lip_w2, lip_h, t, tol, snaps);
        connector();
        // pcb cut-outs
        translate([0, 0, -t]) guts();
    }
    //connector();
    //translate([0, 0, -t]) guts();

}

module bottom() {
    module reinforcement() {
          difference() {
              cylinder(r=t, h=0.7*l);
              translate([0, -0.1, -0.05]) cube([2*t, 2.1*t, 0.81*l]);
              translate([-t, -2*t, -0.05]) cube([2*t, 2*t, 0.81*l]);
              translate([-2.5*t, -0.5, -1.05]) cube([2*t, 2.1*t, 0.81*l]);
          }
    }
 
    difference() {
        rounded_minkowski_inner_lip(l, w, h_b, r, lip_w1, lip_h, t, tol, snaps);
        connector(cutout = "down");
        //translate([8, 8, 3.2]) rotate([0,90,90]) color("black") pj320a(cutout = true);
        //magnets();
    }
   // connector backstop
   translate([-5.7, -3.8, 0]) cube([5, 7, 6]);
  // connector(cutout = "down");

    translate([l/2-1.75*t, w/2-1.0*t+0.1, h_b-t/2-0.175])
       rotate([-90, 0, 90]) reinforcement();

       translate([-l/2+1.75*t, -w/2+1.0*t-0.1, h_b-t/2-0.175])
       rotate([-90, 0, -90]) reinforcement();

  //  translate([0, 0, -t]) guts();
}

echo(str("Rounded Minkowski Box: ", l, "mm x ", w, "mm x ", h_t + h_b, "mm") );

module guts() {
    translate([-0.7, -0.5, 7.8+t]) rotate([0, 0, 180]) gyro_pcb();
    //translate([1.6, 6.6, 4]) straight_header(4,1);
    translate([-0.7, -1.5, 7.5+t]) rotate([0, 0, 0]) color ("red") import("gy-521_pcb.stl");
}

module enclosure () {
    //translate([0, 40, h_t+4.40]) rotate([0, 180, 180])
    //translate([0, 0, t+0.3])
    translate([0, 0, 20])
    color("white") top();

    translate([0, 0, t])
    color("green") bottom();

    translate([0, 0, 6])
    guts();

}

//difference() {
enclosure();
//translate([0, 40, h_t+4.40]) rotate([0, 180, 180])
//top();
//bottom();
//translate([5, 5, 0]) cube([50, 50, 50]);
//}

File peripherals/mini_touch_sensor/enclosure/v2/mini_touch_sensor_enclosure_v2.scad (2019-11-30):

/* red_touch_sensor_enclosure.scad
 *
 *    OpenSCAD script to generate an enclosure for red touch sensor board
 *
 *    Copyright 2018 Don Haig (time4tux at gmail dot com)
 *
 *    GNU GPLv3 (See LICENSE for details) 
 *
 */
$fn = 50;

use<red_touch_sensor.scad>
use<pj320a.scad>
use<rounded_minkowski_box.scad>
use<straight_header.scad>

u_d_pcb = 1.9;  // up - down adjustment on z-axis for PCB


/* 3D printer parameters */                                                                                                                      
    nozzle_diam = 0.4;    // 3D printer nozzle diameter in mm                                                                                         
    layer_res = 0.1;      // 3D printer layer resolution in mm                                                                                              

/* Enclosure Dimensions */
    tol = 0.01;                // printing tolerance (should be evenly divisible by nozzle diameter)
    lip_w1 = 1.2;              // thickness of outer lip (should be evenly divisible by nozzle diameter)
    lip_w2 = 1.2;              // thickness of inner lip (should be evenly divisible by nozzle diameter)
    t = lip_w1+lip_w2;         // total wall thickness (should be evenly divisible by nozzle diameter)
    l = 16.8+2*t;              // Outside Length of enclosure (should be evenly divisible by nozzle diameter)
    w = 14 + 2*t;              // Outside width of enclosure (should be evenly divisible by nozzle diameter)
    h_t = 8.0;                   // height of top piece of enclosure (should be evenly divisible by layer resolution)
    h_b = 6.8;                  // height of bottom piece of enclosure (should be evenly divisible by layer resolution)
    r = 2;                     // Outside corner radius
    lip_h = 2;               // height of lip (should be evenly divisible by layer resolution)


    check_dimension(l, nozzle_diam);
    check_dimension(w, nozzle_diam);
    check_dimension(t, nozzle_diam);
    check_dimension(lip_w1, nozzle_diam);
    check_dimension(lip_w2, nozzle_diam);

    check_dimension(h_t, layer_res);
    check_dimension(h_b, layer_res);
    check_dimension(lip_h, layer_res);


    // snaps parameter can have the following values:                                                                                                 
    // "normal"  - bumps on lid, recesses on the bottom piece of enclosure
    // "reverse" - recesses on lid, bumps on the bottom piece of enclosure
    // "NORMAL" -  larger recesses on lid, larger bumps on the bottom piece of enclosure
    // "REVERSE" - larger recesses on lid, larger bumps on the bottom piece of enclosure

module connector(cutout) {

      translate([9.0, 0, 6.1])
     rotate([0,180,90]) color("black") pj320a(cutout);
}


module top() {
    module cut_out() {
        l = 12;
        w = 10;
        h = 1.8;

        translate ([0, -0, 10])
        difference() {
            minkowski() {
                color("white") cube([l, w, h], center=true);
                cylinder(r=2, h=h, center = true);
            }
        }
    }

    difference() {
        translate([0, 0, h_t+2])
        rotate([0, 180, 0])
        rounded_minkowski_outer_lip(l, w, h_t, r, lip_w2, lip_h, t, tol, "REVERSE");
        connector();
        // pcb cut-outs
        color("blue") cut_out();
        //translate([-6, 0, 1]) cube([1.2, 8, 20], center=true);
    }
        //translate([-6, 0, -1]) cube([1.2, 8, 20], center=true);
   // translate([0, 0, -t]) guts();

}

module bottom() {
    difference() {
        rounded_minkowski_inner_lip(l, w, h_b, r, lip_w1, lip_h, t, tol, "REVERSE");
        connector(cutout = "down");
        //translate([8, 8, 3.2]) rotate([0,90,90]) color("black") pj320a(cutout = true);
        //magnets();
        translate([0, 0, h_b]) cube([l, w, 3],center=true);
    }
   // connector backstop
  // connector(cutout = "down");
}

echo(str("Rounded Minkowski Box: ", l, "mm x ", w, "mm x ", h_t + h_b, "mm") );

module guts() {
    rotate([0, 0, 90]) {
        translate([0, 0, 10.1+t]) red_sensor_pcb();
        translate([-13.1, -8.8, 7.5+t]) rotate([0, 0, 180]) color ("red") import("red_touch_sensor_trrs_pcb.stl");
    }
}

module enclosure () {
    //translate([0, 30, h_t+2*t-0.40]) rotate([0, 180, 180])
    //translate([0, 0, t+0.3])
    translate([0, 0, 15])
    color("white")top();

    //translate([0, 0, t])
    color("yellow")bottom();

    guts();

}

//difference() {
enclosure();
//translate([5, 5, 0]) cube([50, 50, 50]);
//}

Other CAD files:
peripherals/lightbox/enclosure/v3/stl_files/connector_test.stl
peripherals/mini_touch_sensor/enclosure/v2/red_touch_sensor.stl
peripherals/mini_touch_sensor/enclosure/v2/stl_files/mini_touch_bottom_v2.stl
peripherals/mini_touch_sensor/red_touch_sensor_trrs_pcb/red_touch_sensor_trrs_pcb.FCStd
peripherals/mini_touch_sensor/enclosure/v2/red_touch_sensor.scad
controllers/atmega32u4/enclosure/v1.2.2/enclosure.scad
controllers/atmega32u4/enclosure/v1.2.2/pcb.scad
controllers/atmega32u4/enclosure/v1.2.2/stl_files/top.stl
controllers/leonardo/enclosure/enclosure.scad
controllers/leonardo/enclosure/pcbs.scad
controllers/leonardo/enclosure/stl_files/v2/enclosure_bottom_v2.stl
openscad/captive_nut.scad
openscad/pj320a.scad
openscad/rounded_box1.scad
openscad/rounded_box2.scad
openscad/rounded_minkowski_box.scad
openscad/straight_header.scad
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

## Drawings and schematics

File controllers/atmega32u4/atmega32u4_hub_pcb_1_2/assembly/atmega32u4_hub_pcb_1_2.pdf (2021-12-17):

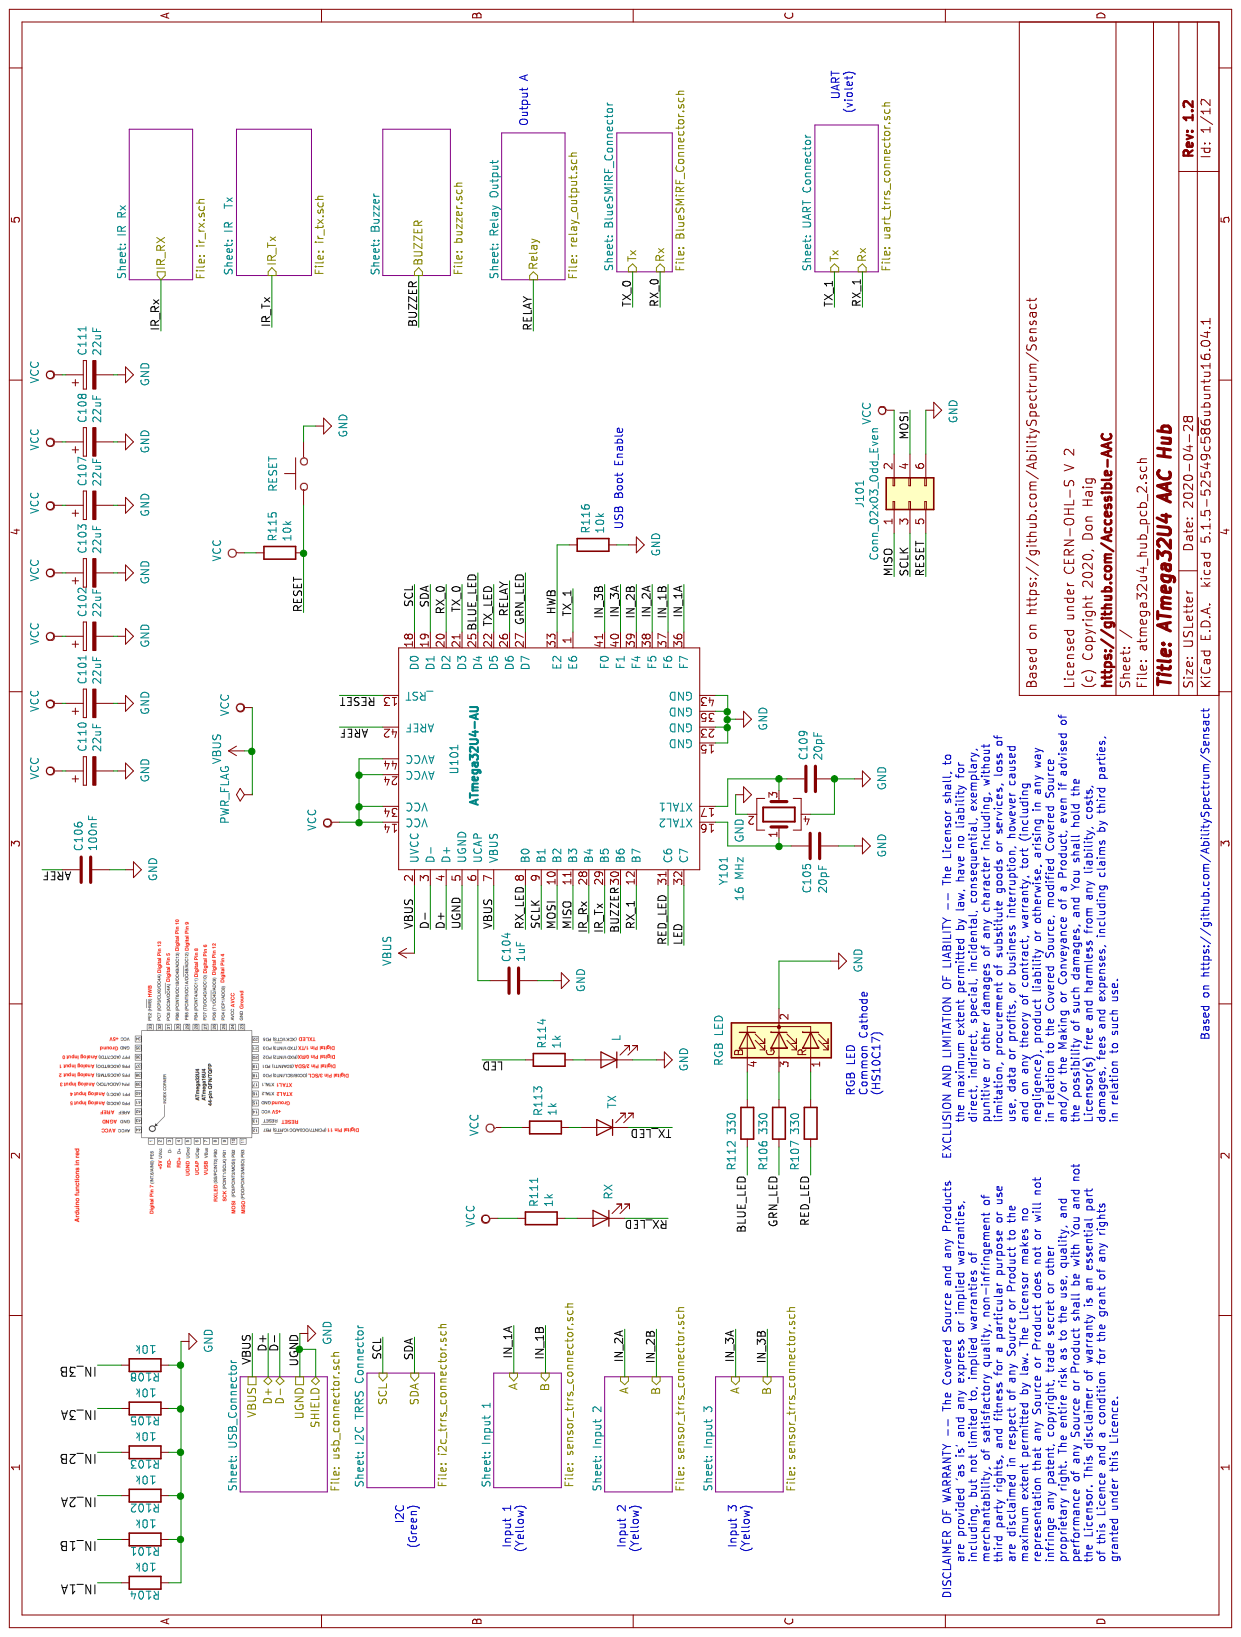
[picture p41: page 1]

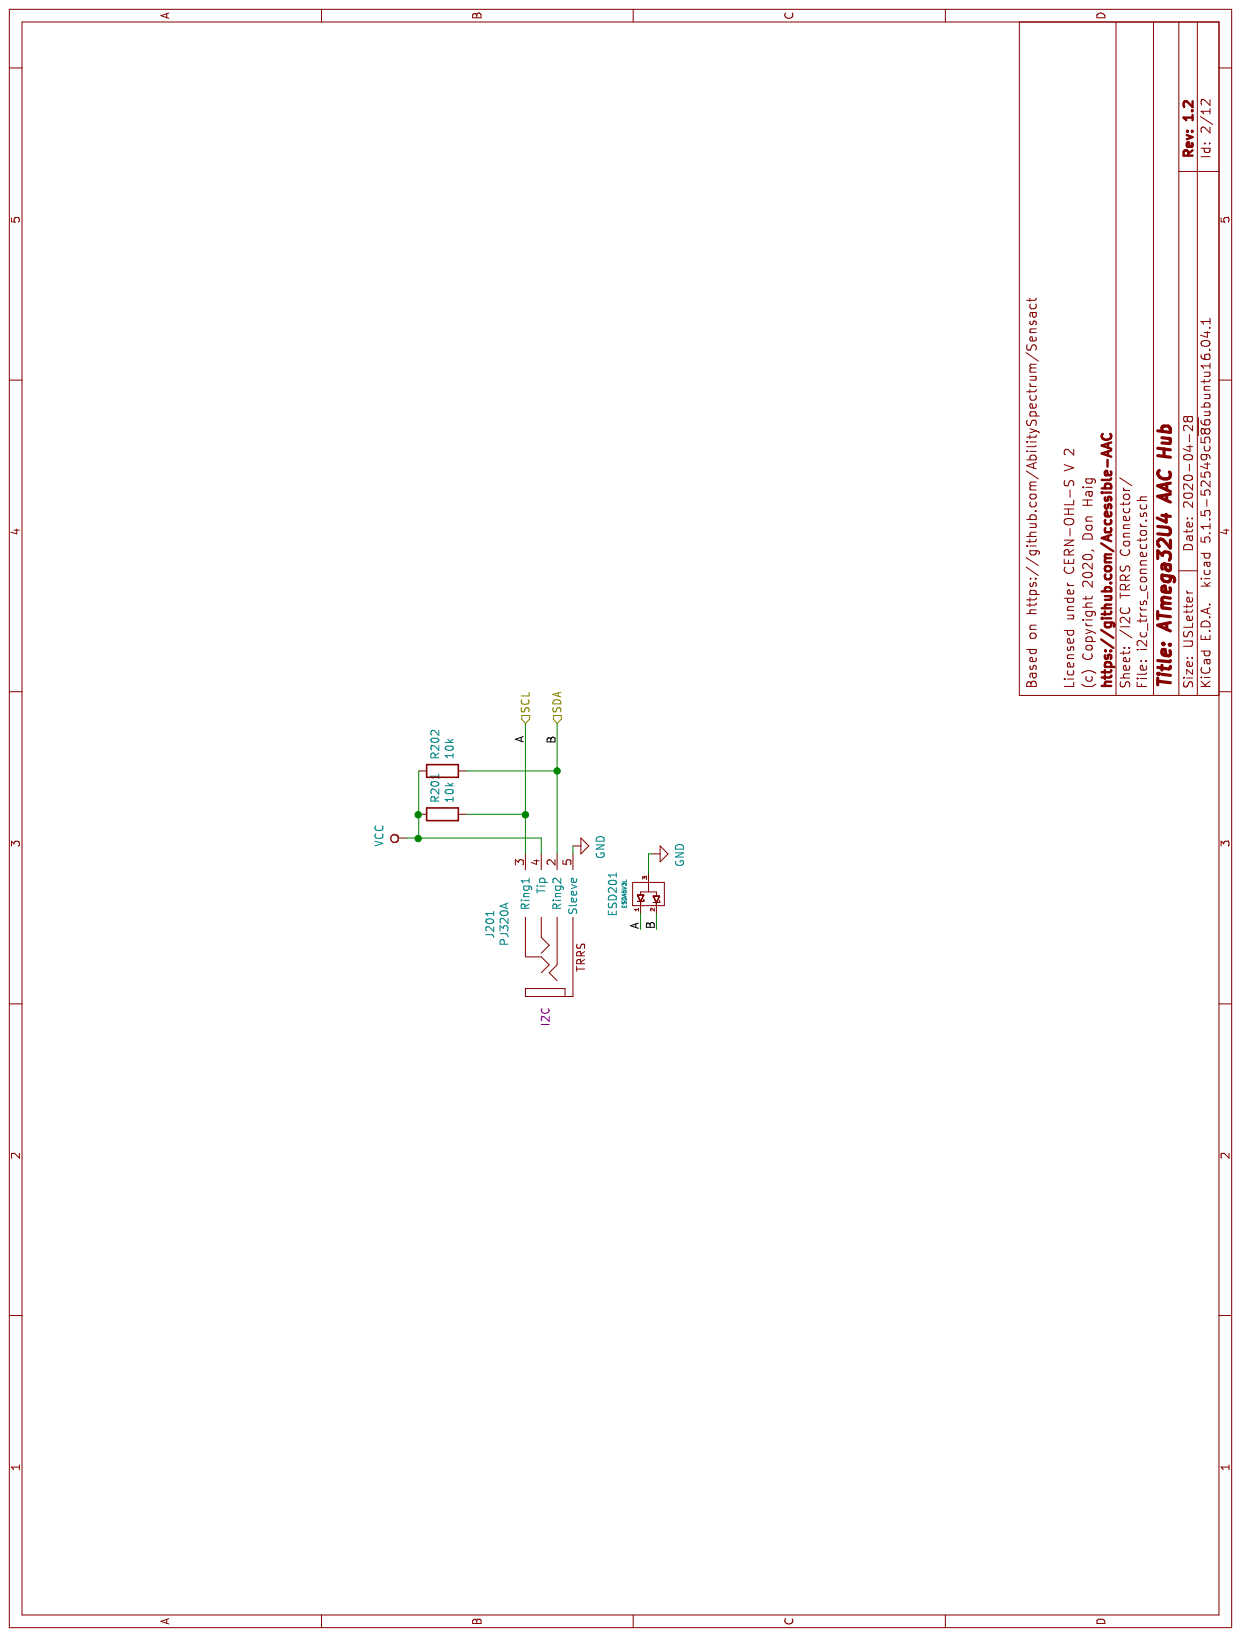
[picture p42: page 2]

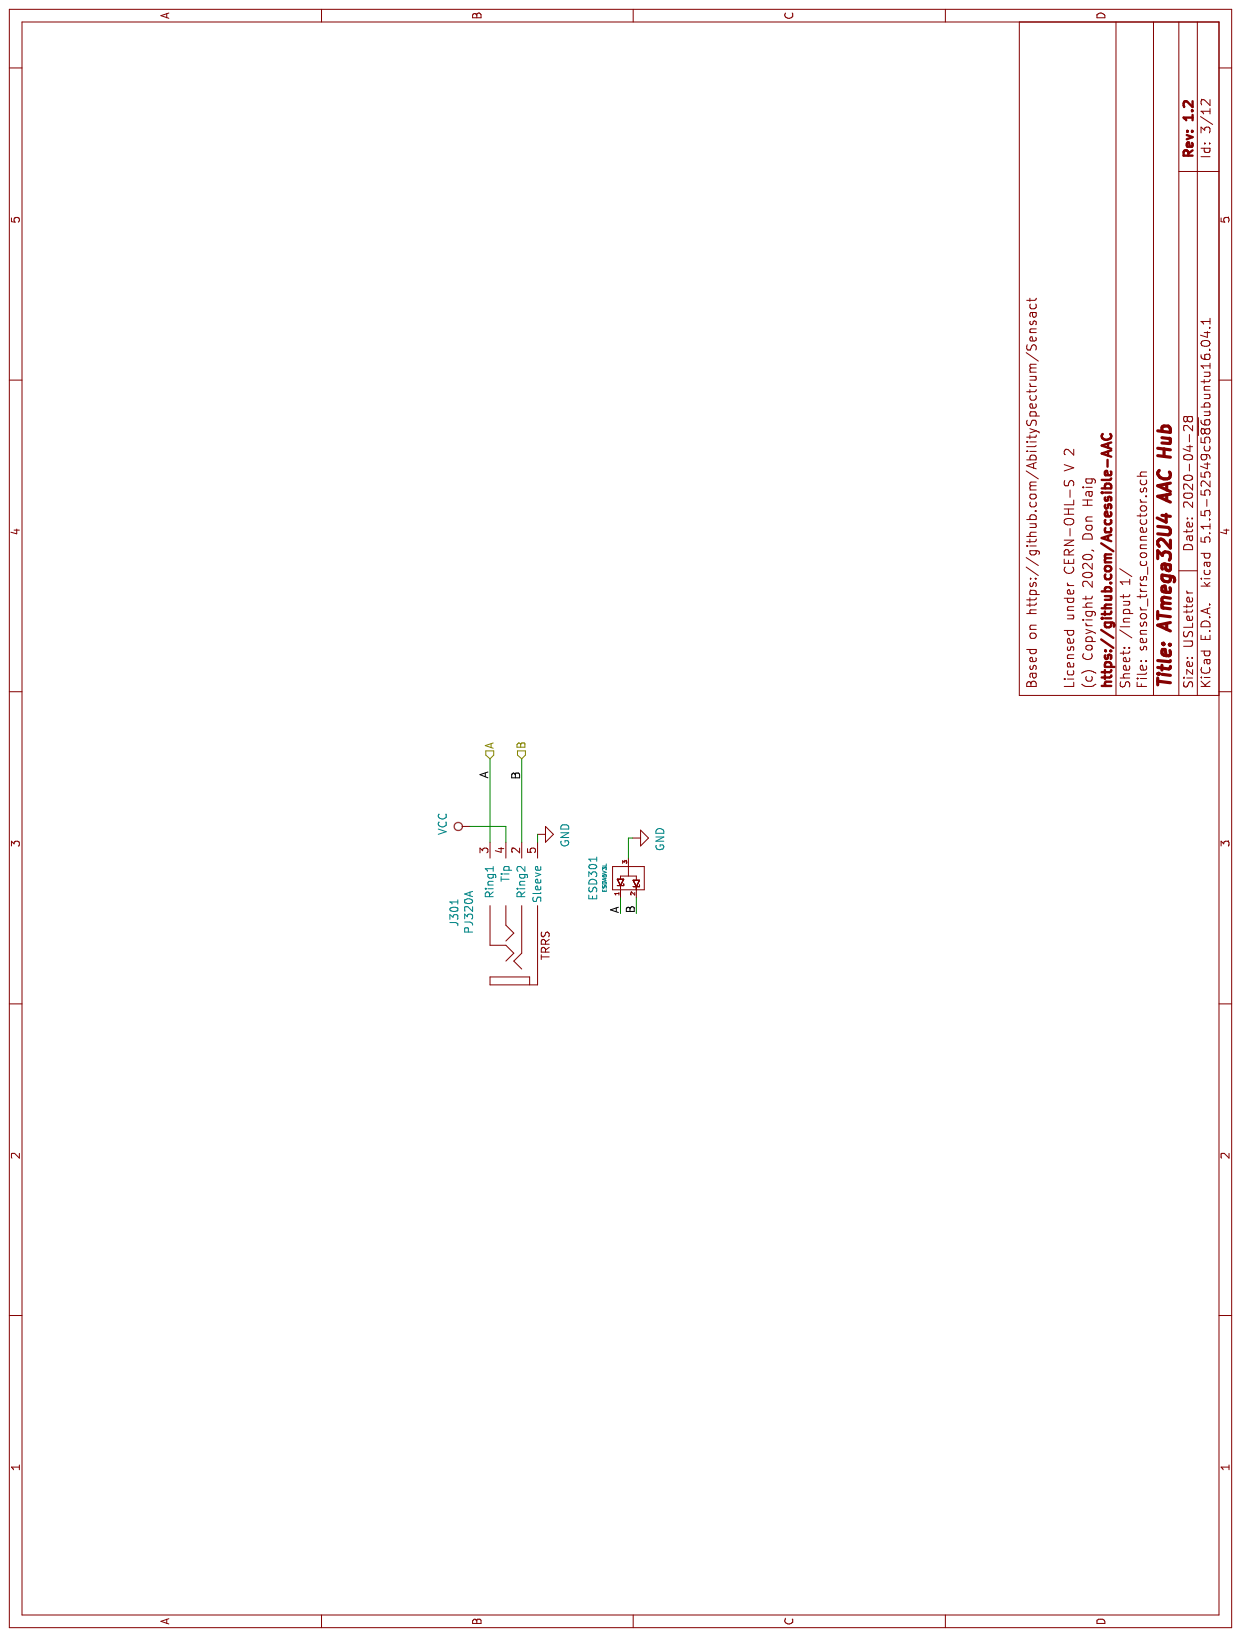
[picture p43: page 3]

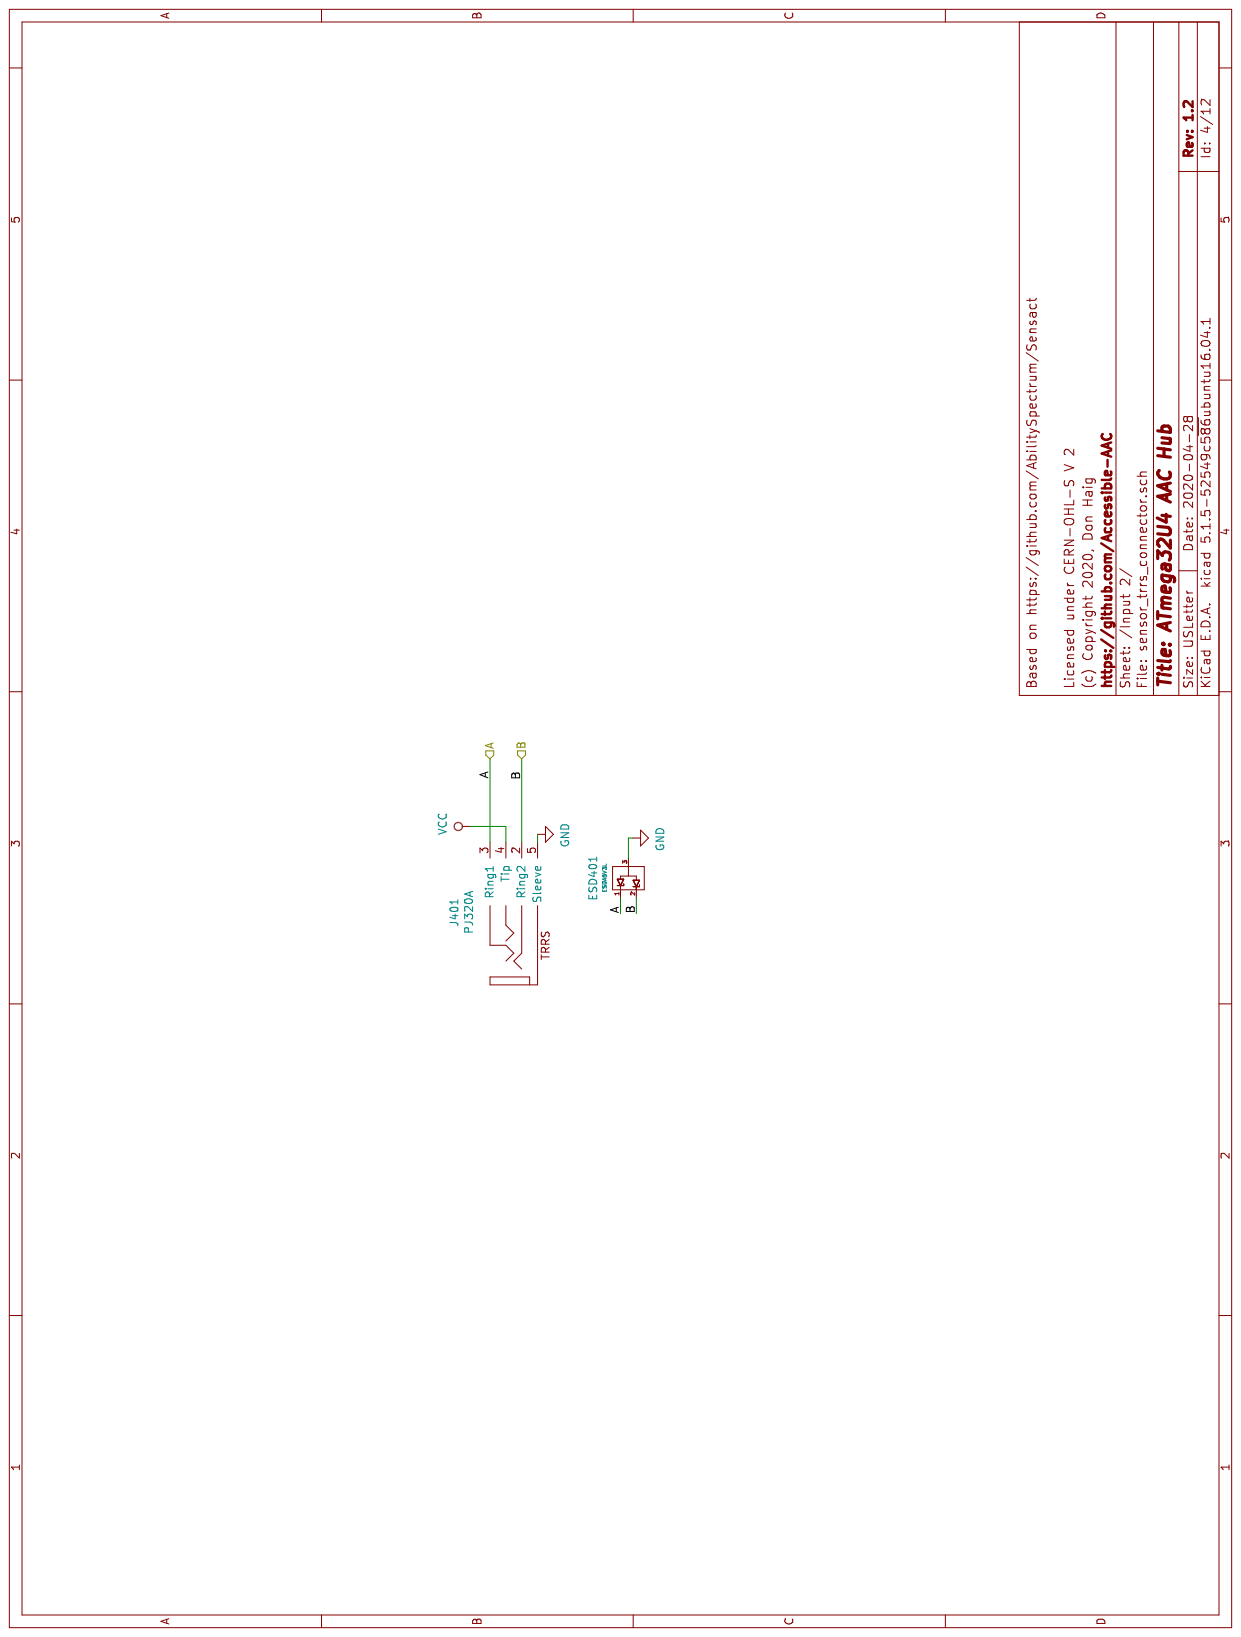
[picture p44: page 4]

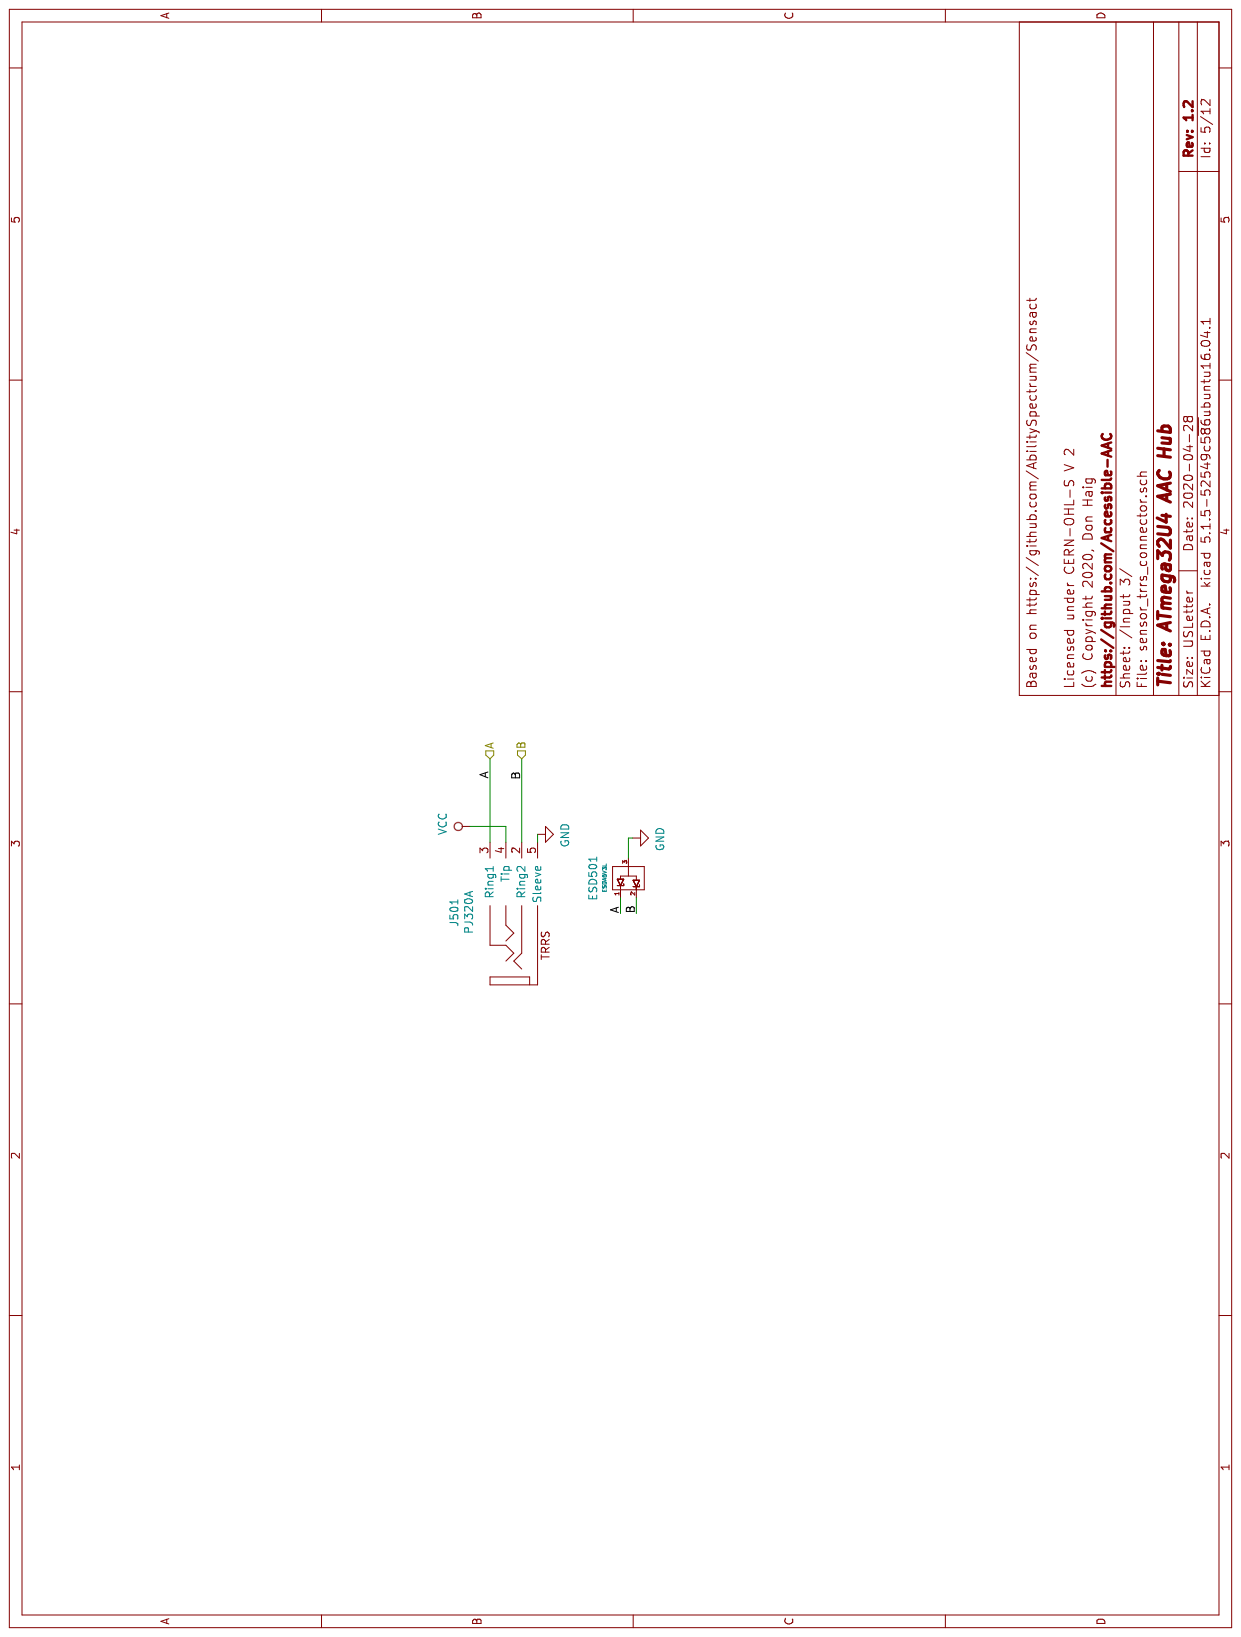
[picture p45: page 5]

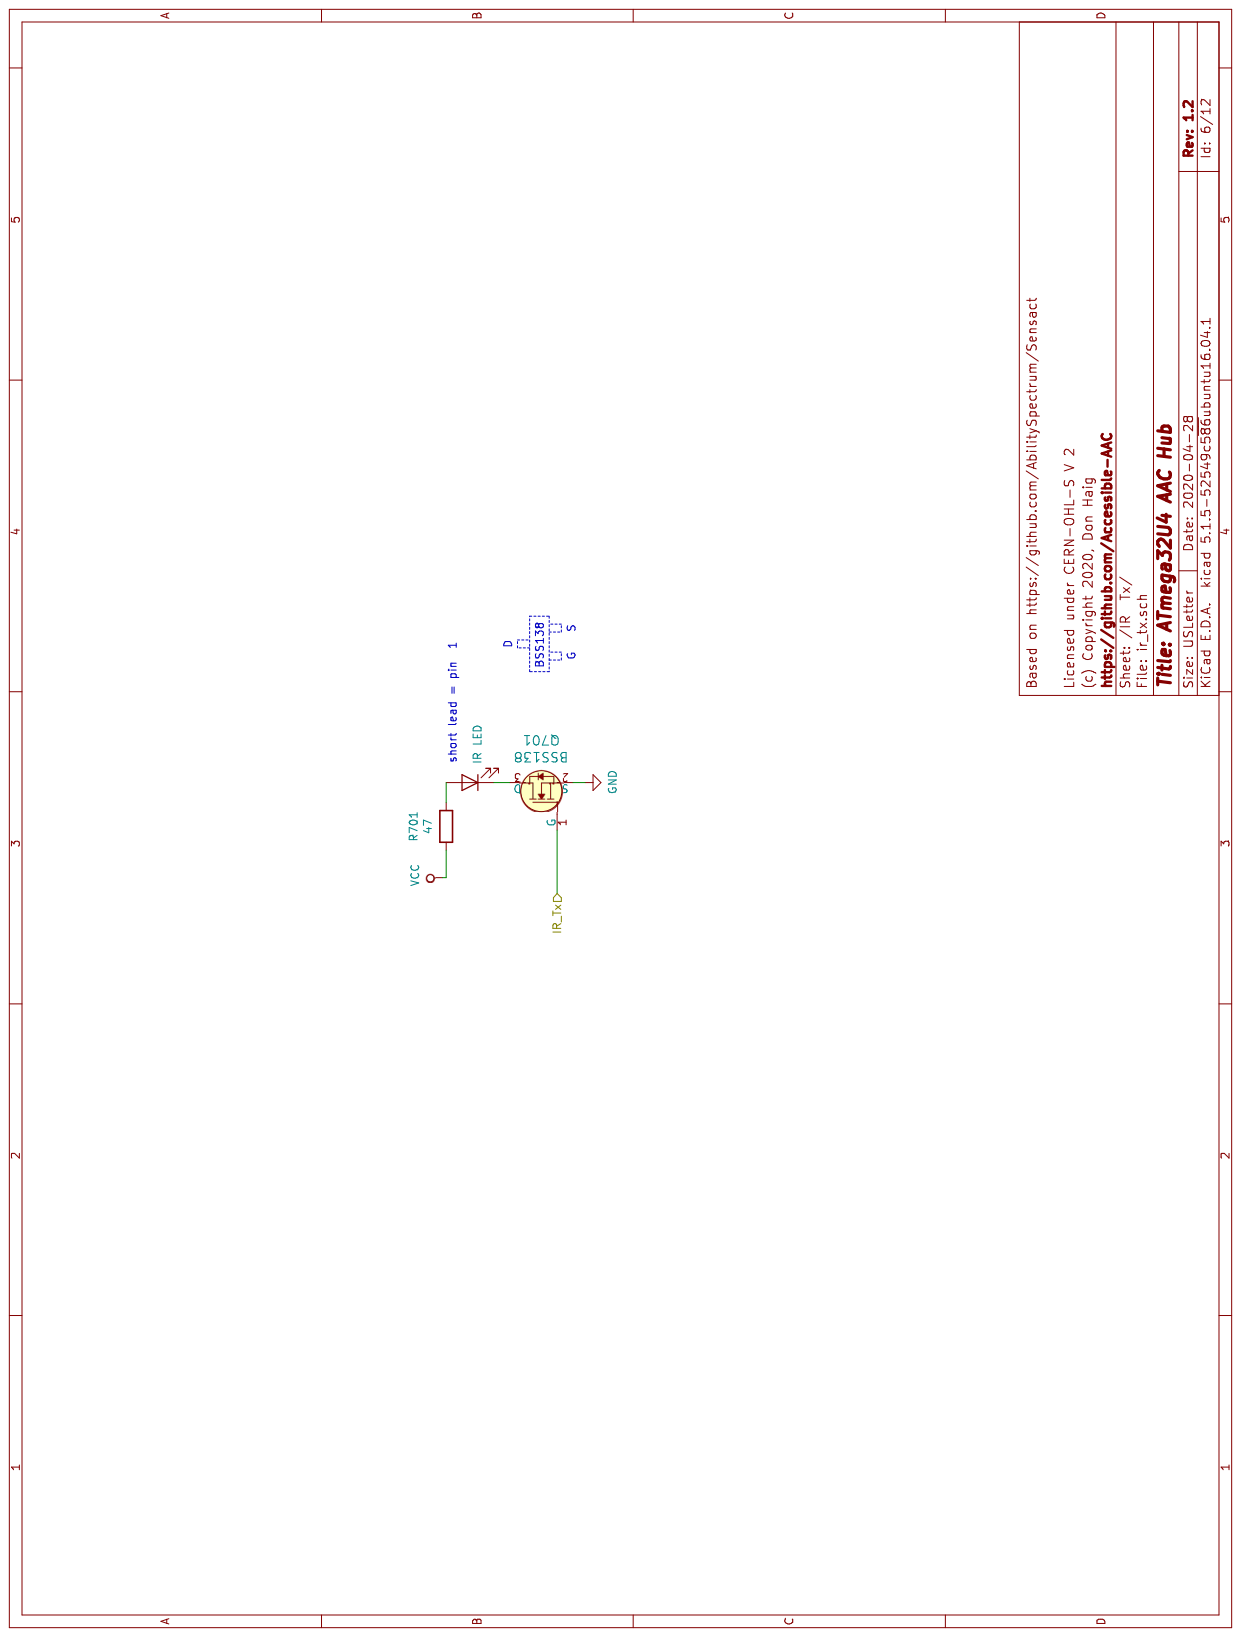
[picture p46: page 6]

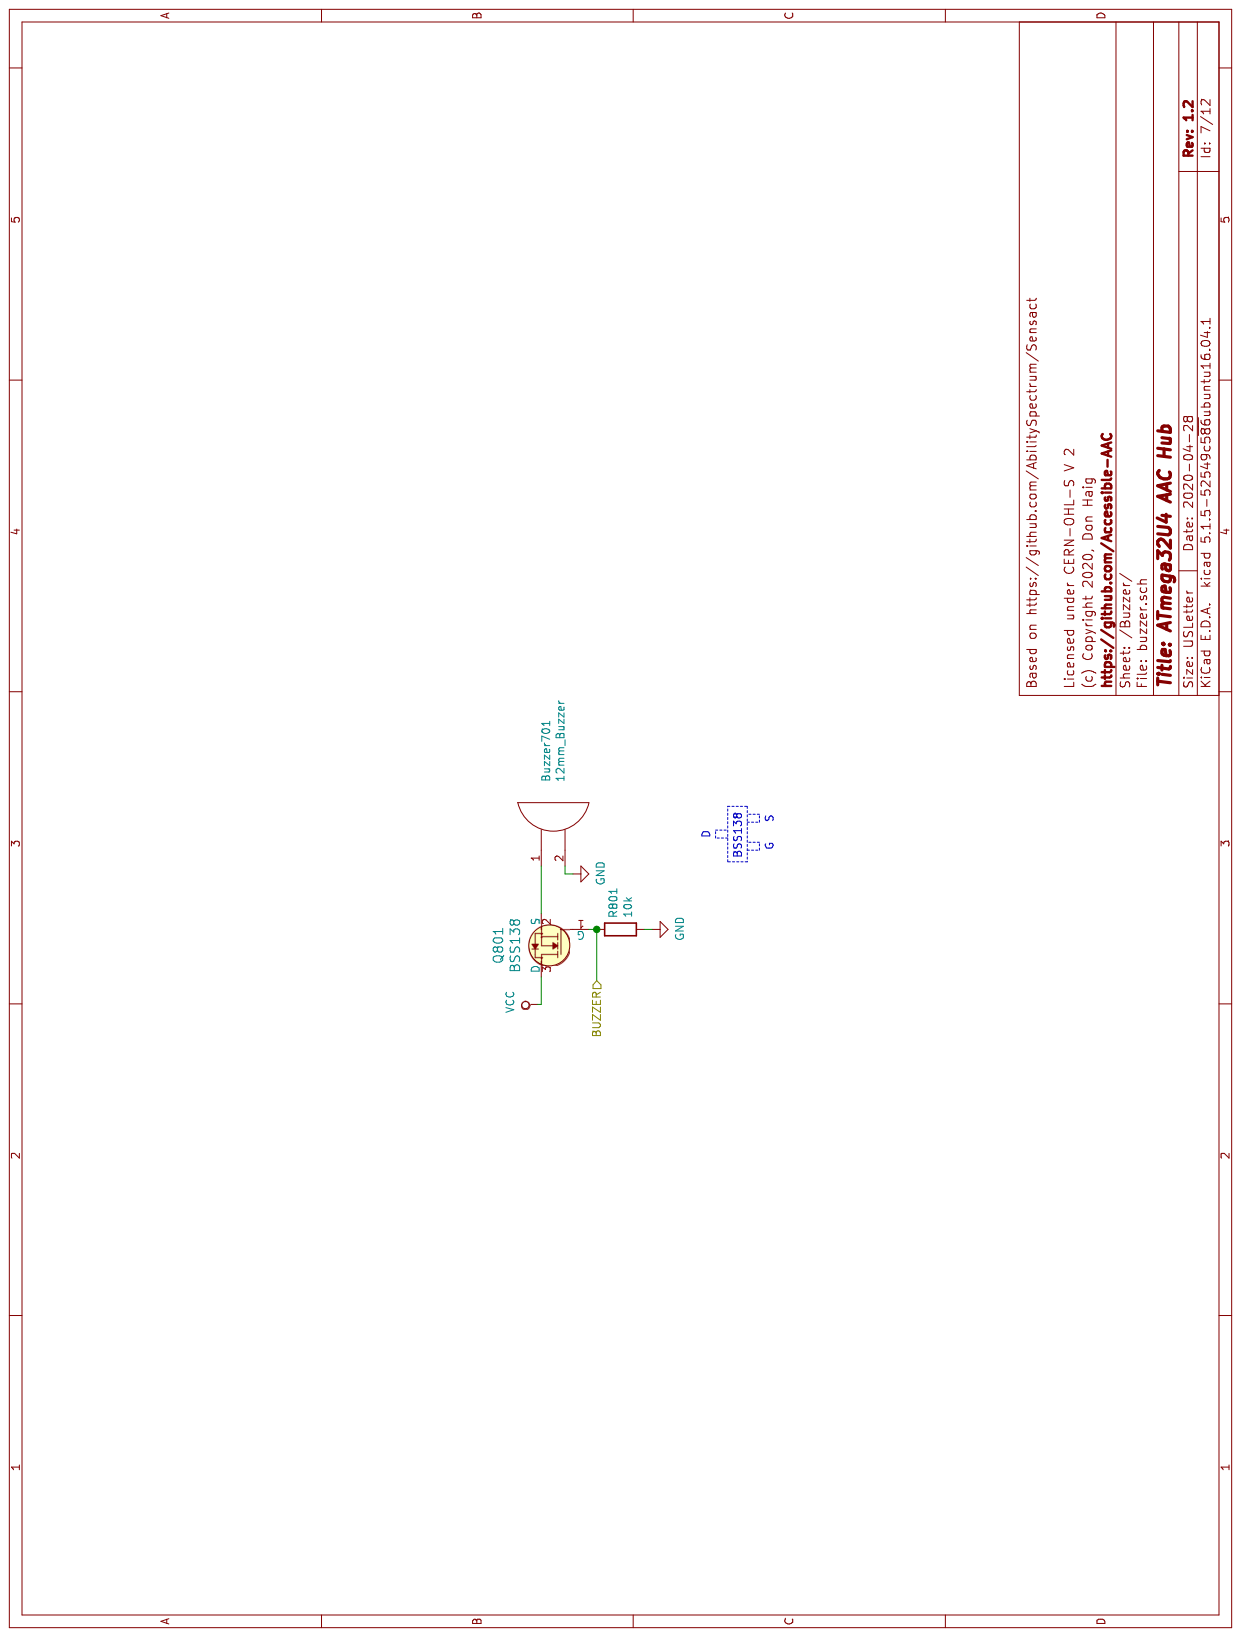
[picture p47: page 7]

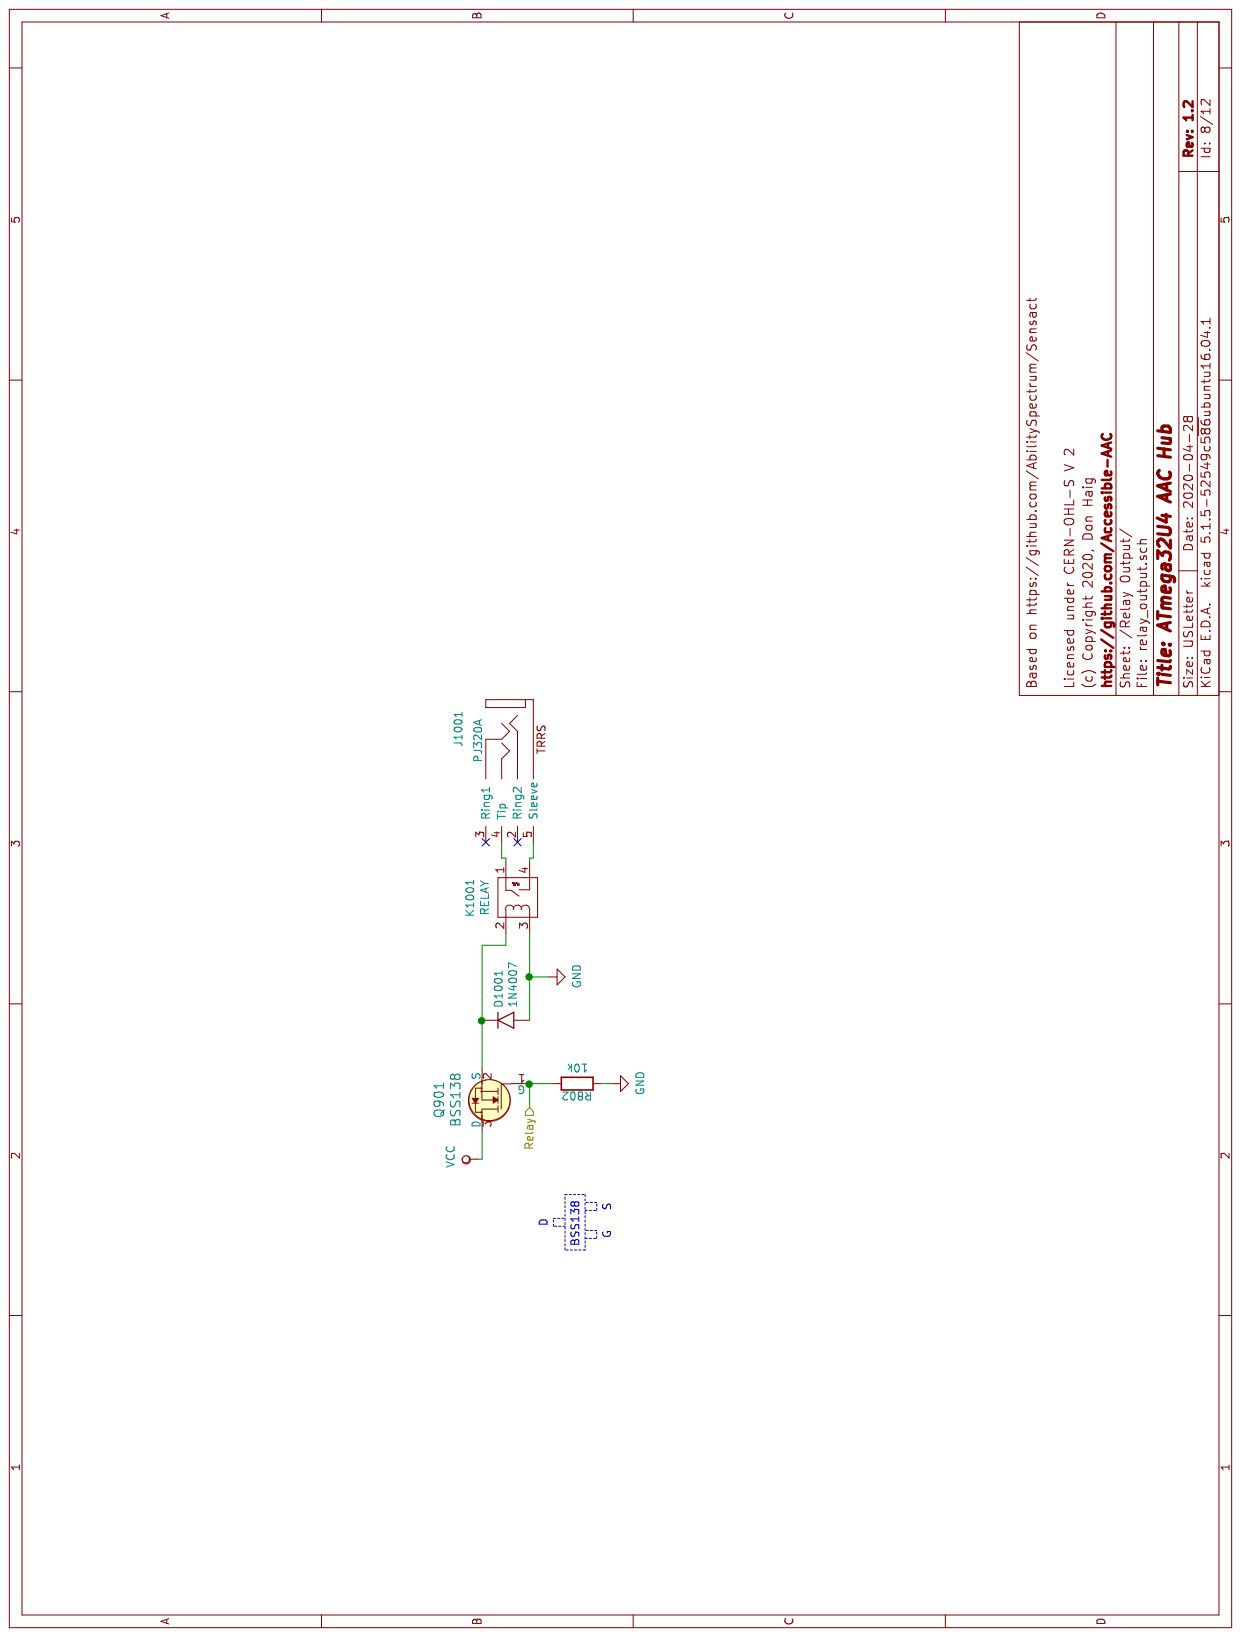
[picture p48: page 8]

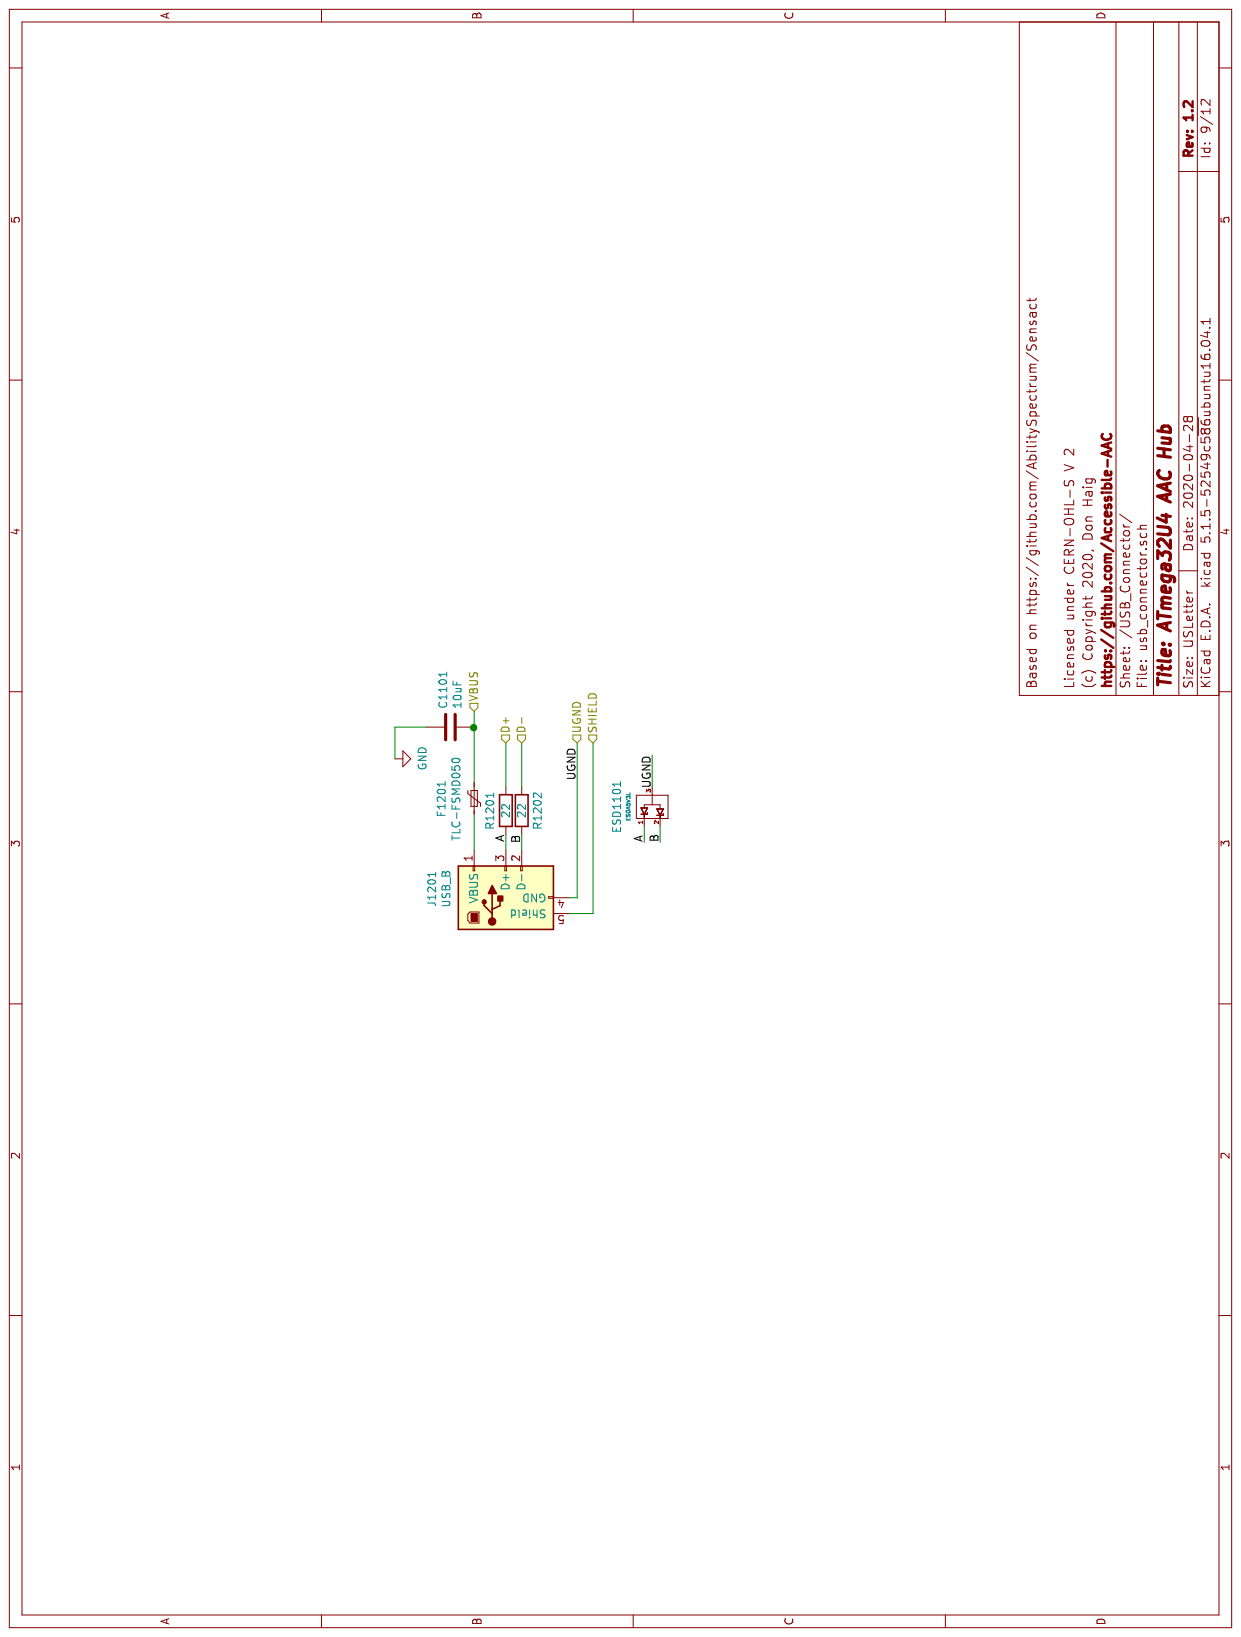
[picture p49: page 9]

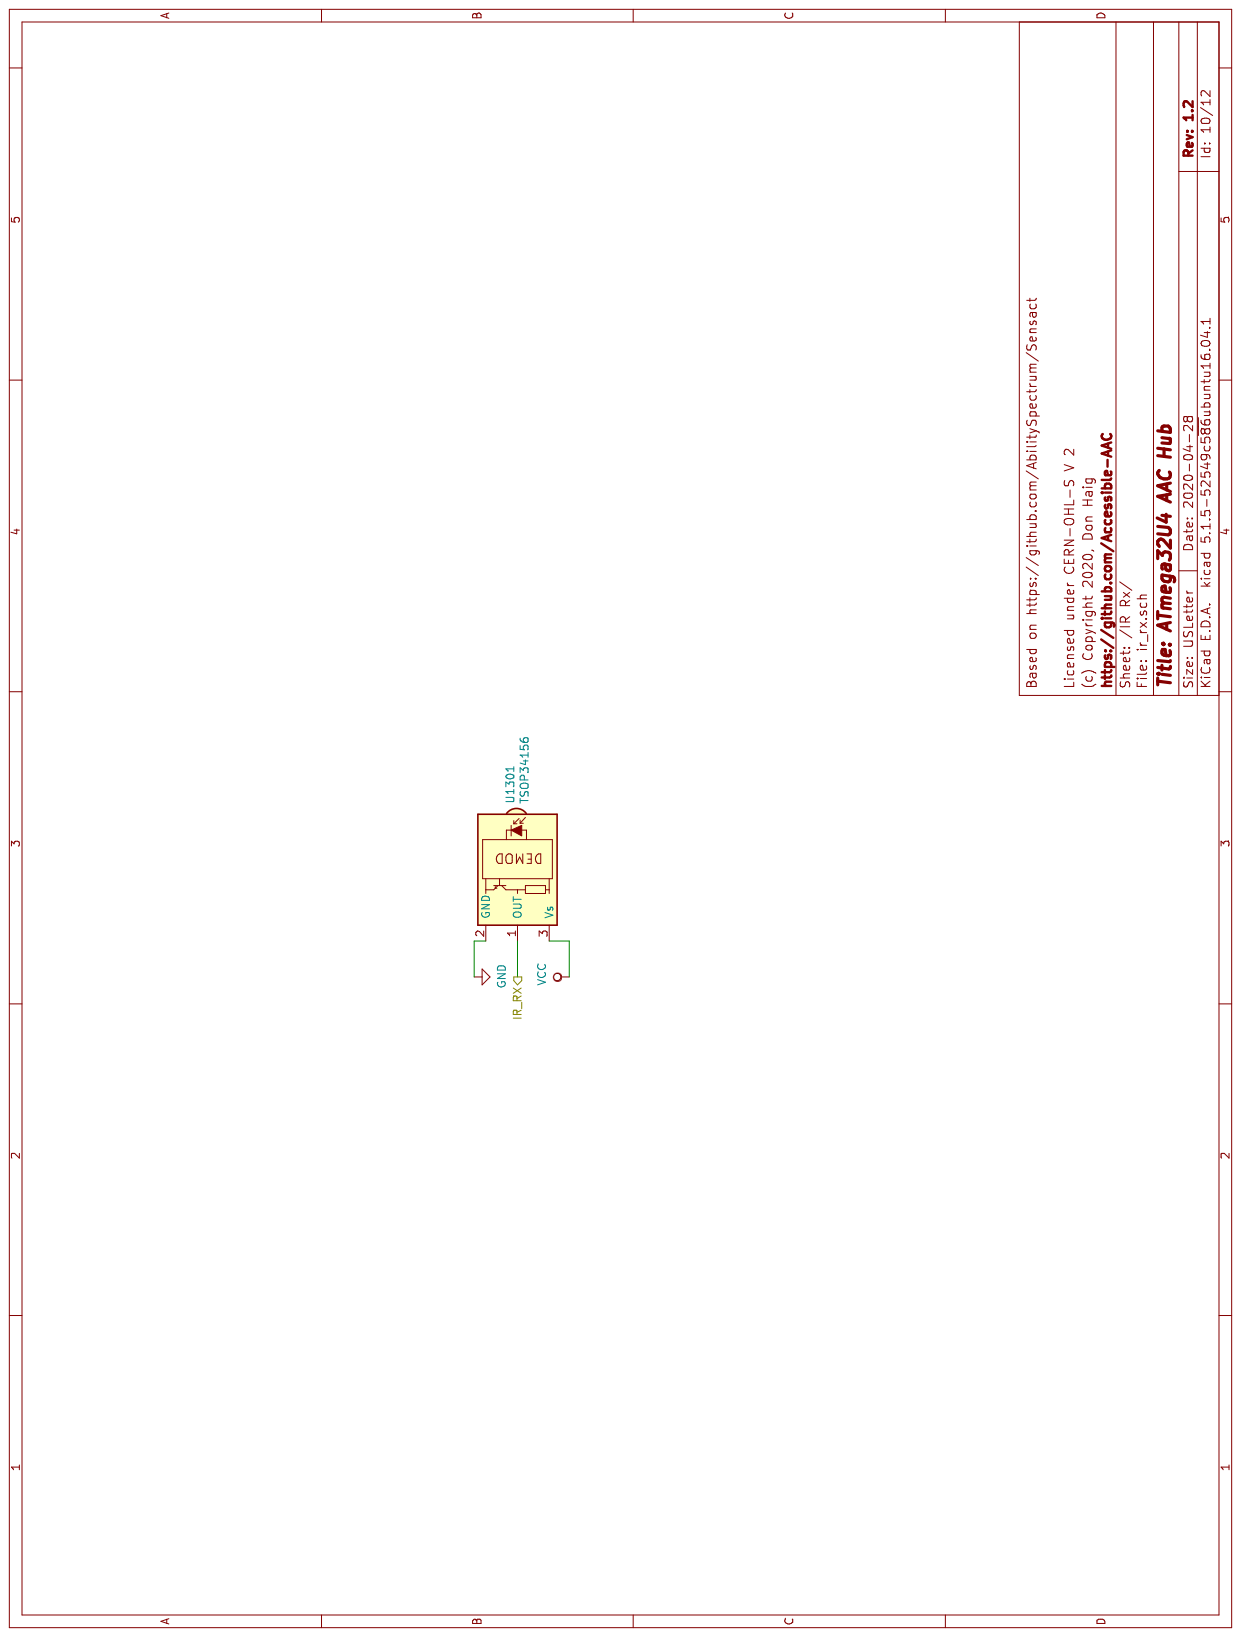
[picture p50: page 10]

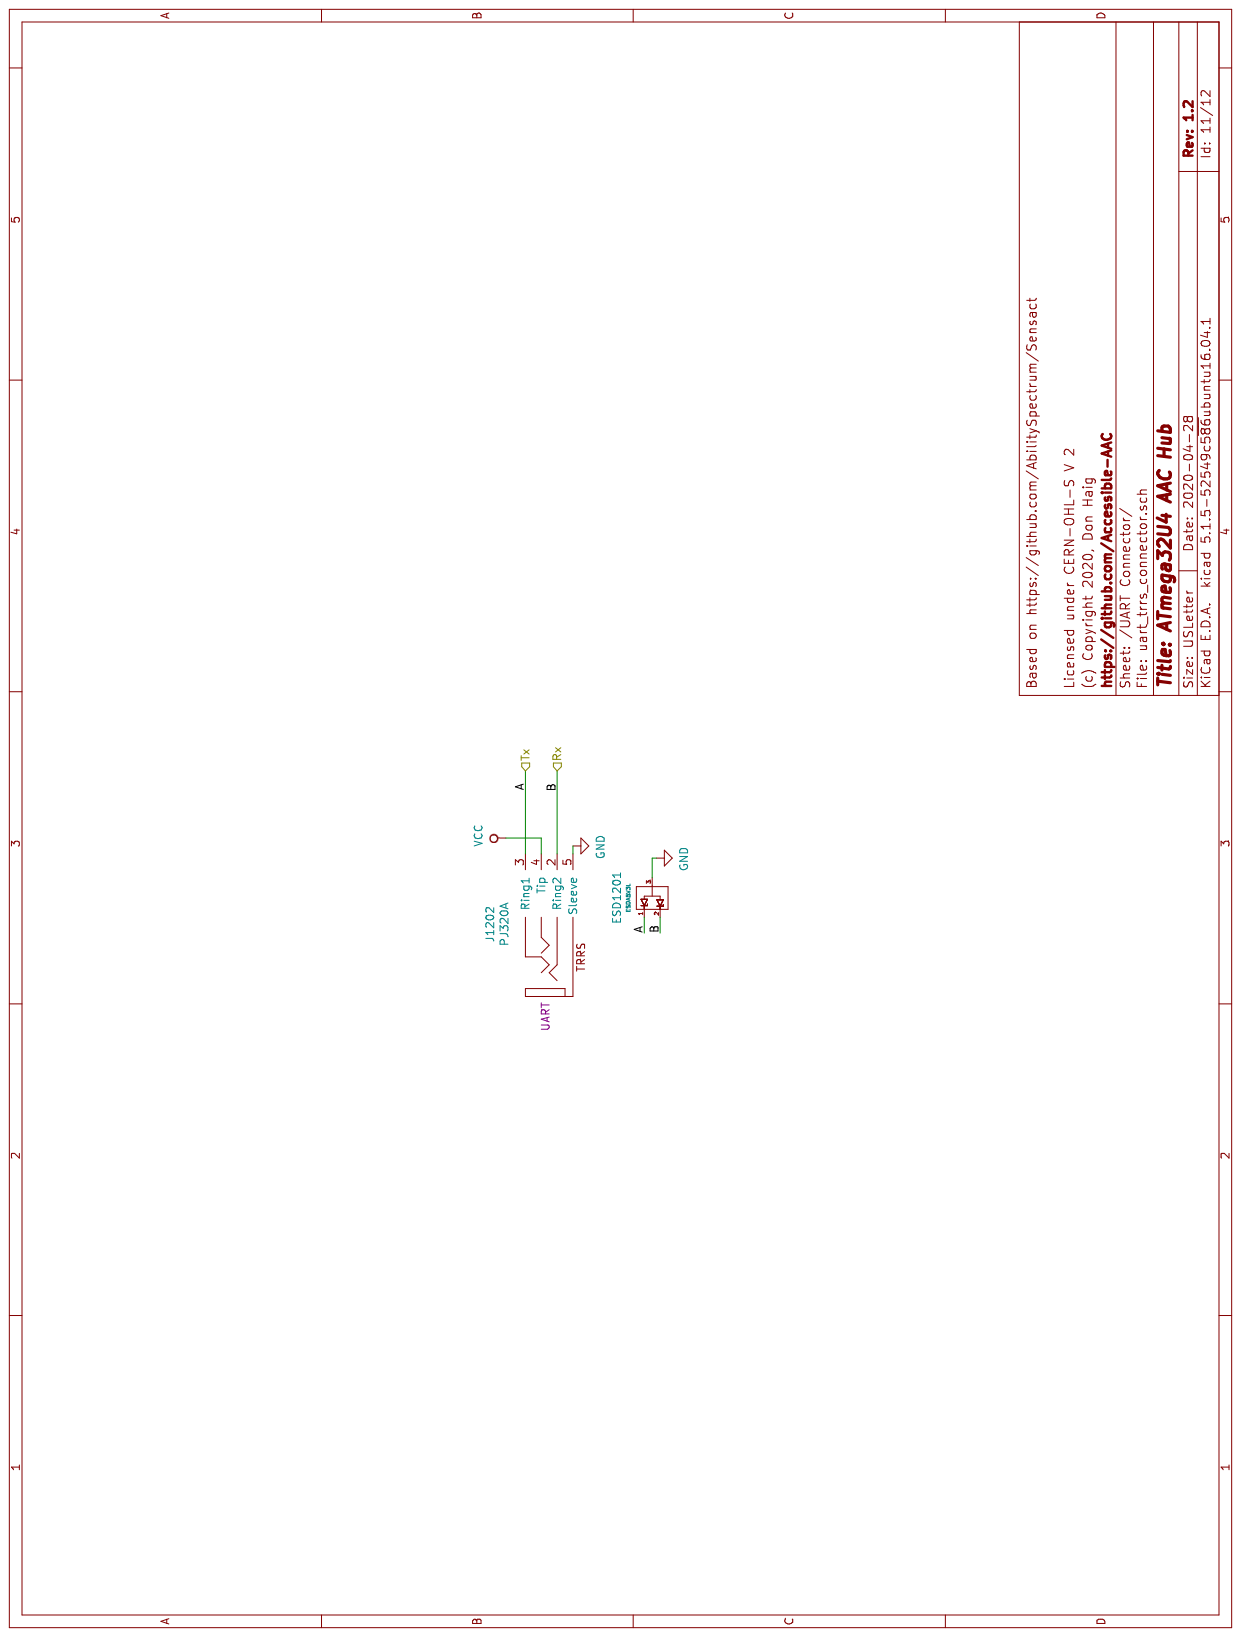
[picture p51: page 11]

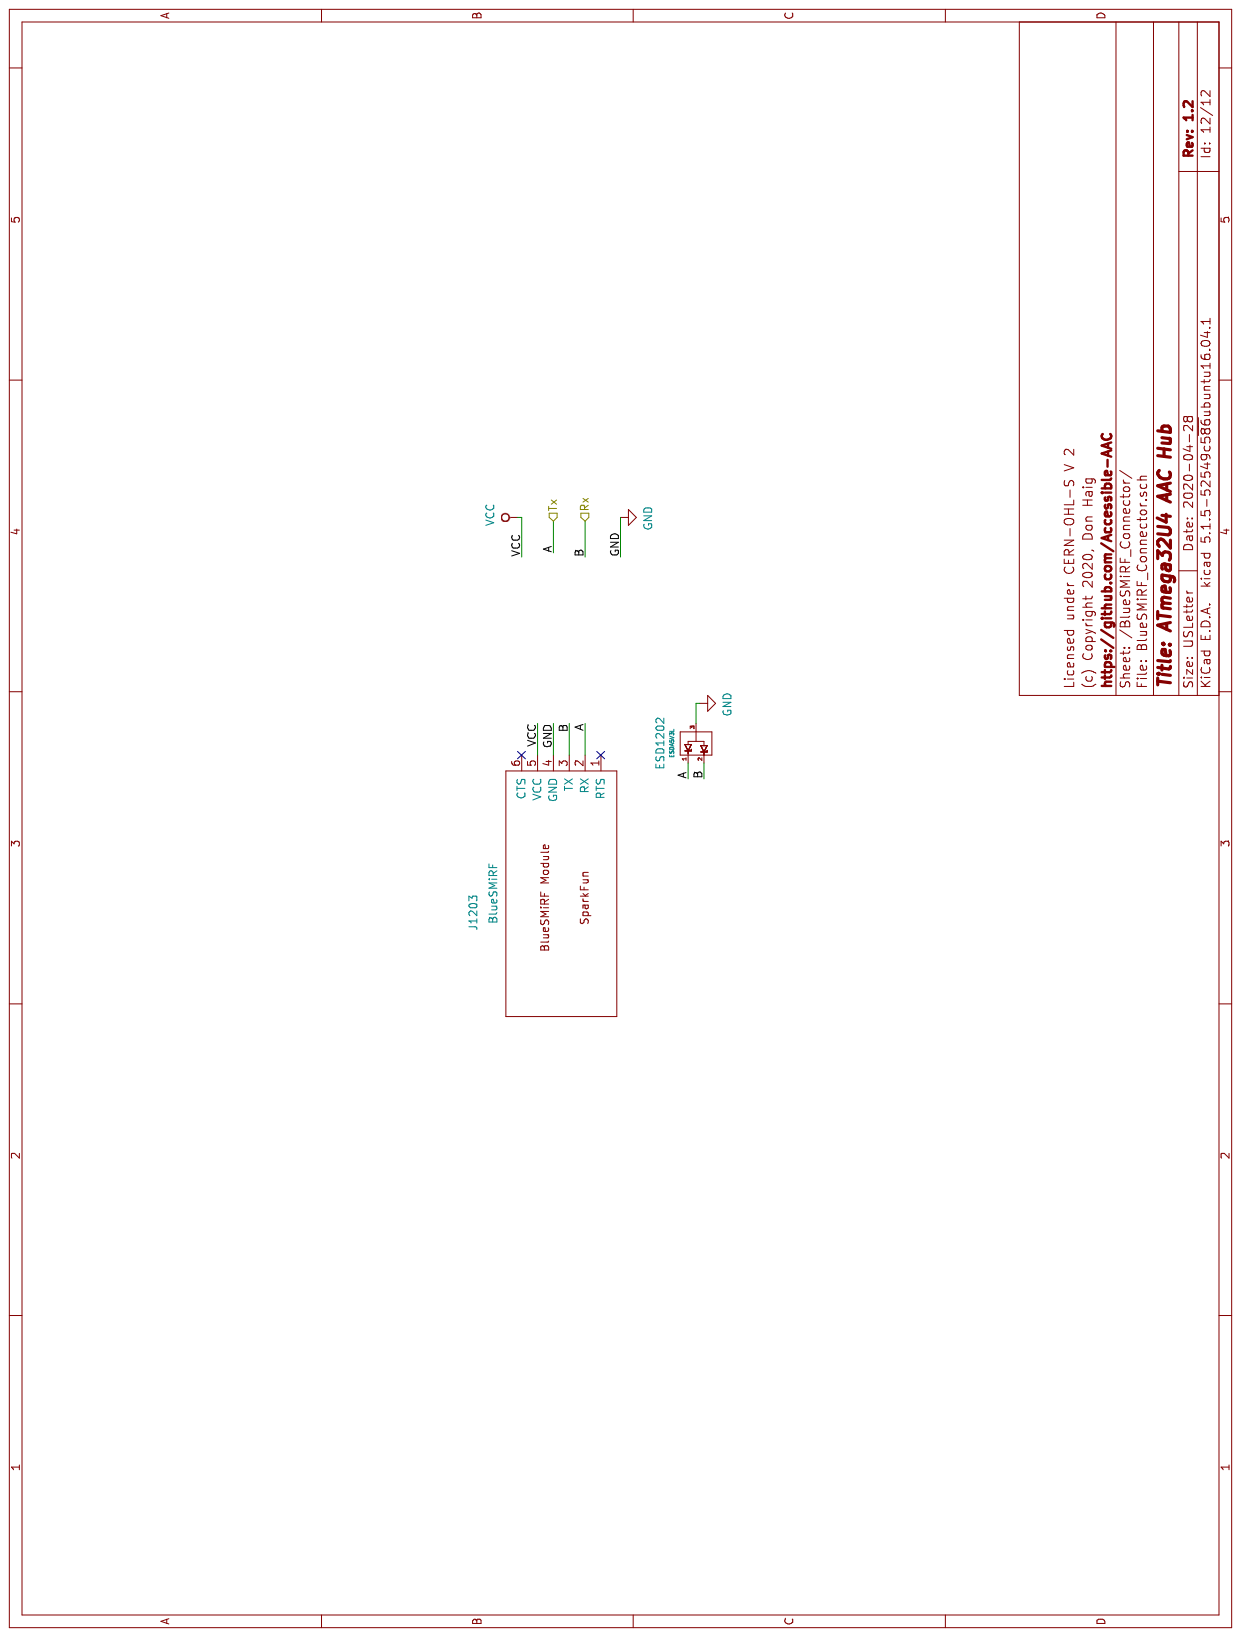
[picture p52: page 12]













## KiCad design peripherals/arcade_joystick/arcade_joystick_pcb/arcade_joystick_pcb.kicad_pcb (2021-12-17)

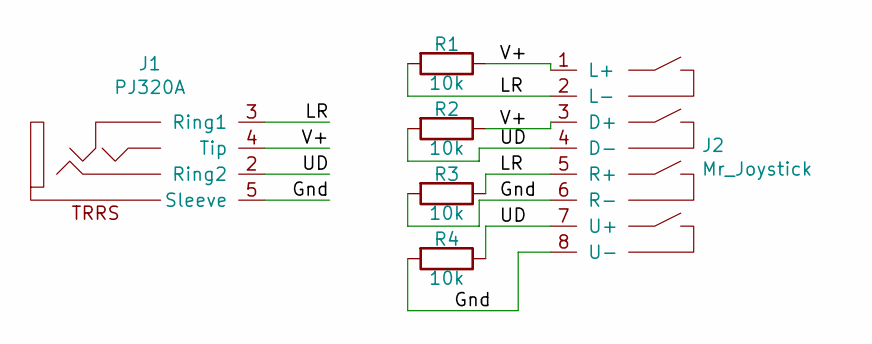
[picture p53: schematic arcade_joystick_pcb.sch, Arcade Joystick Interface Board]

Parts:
J1: PJ320A; PJ-320A
J2: Mr_Joystick
R1, R2, R3, R4: 10k; R_1206_3216Metric; LCSC C17902

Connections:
/Gnd: J1.5 (Sleeve), J2.6 (R-), J2.8 (U-), R3.2, R4.2
/LR: J1.3 (Ring1), J2.2 (L-), J2.5 (R+), R1.2, R3.1
/UD: J1.2 (Ring2), J2.4 (D-), J2.7 (U+), R2.2, R4.1
/V+: J1.4 (Tip), J2.1 (L+), J2.3 (D+), R1.1, R2.1

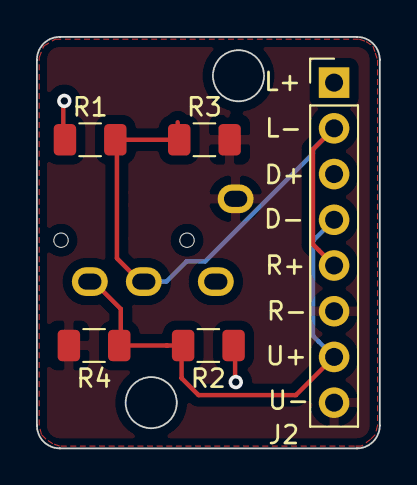
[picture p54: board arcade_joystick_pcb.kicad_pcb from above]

Board: 2 copper layers, 19.1 x 22.9 mm, 6 parts (1 on the bottom side), 4 nets.

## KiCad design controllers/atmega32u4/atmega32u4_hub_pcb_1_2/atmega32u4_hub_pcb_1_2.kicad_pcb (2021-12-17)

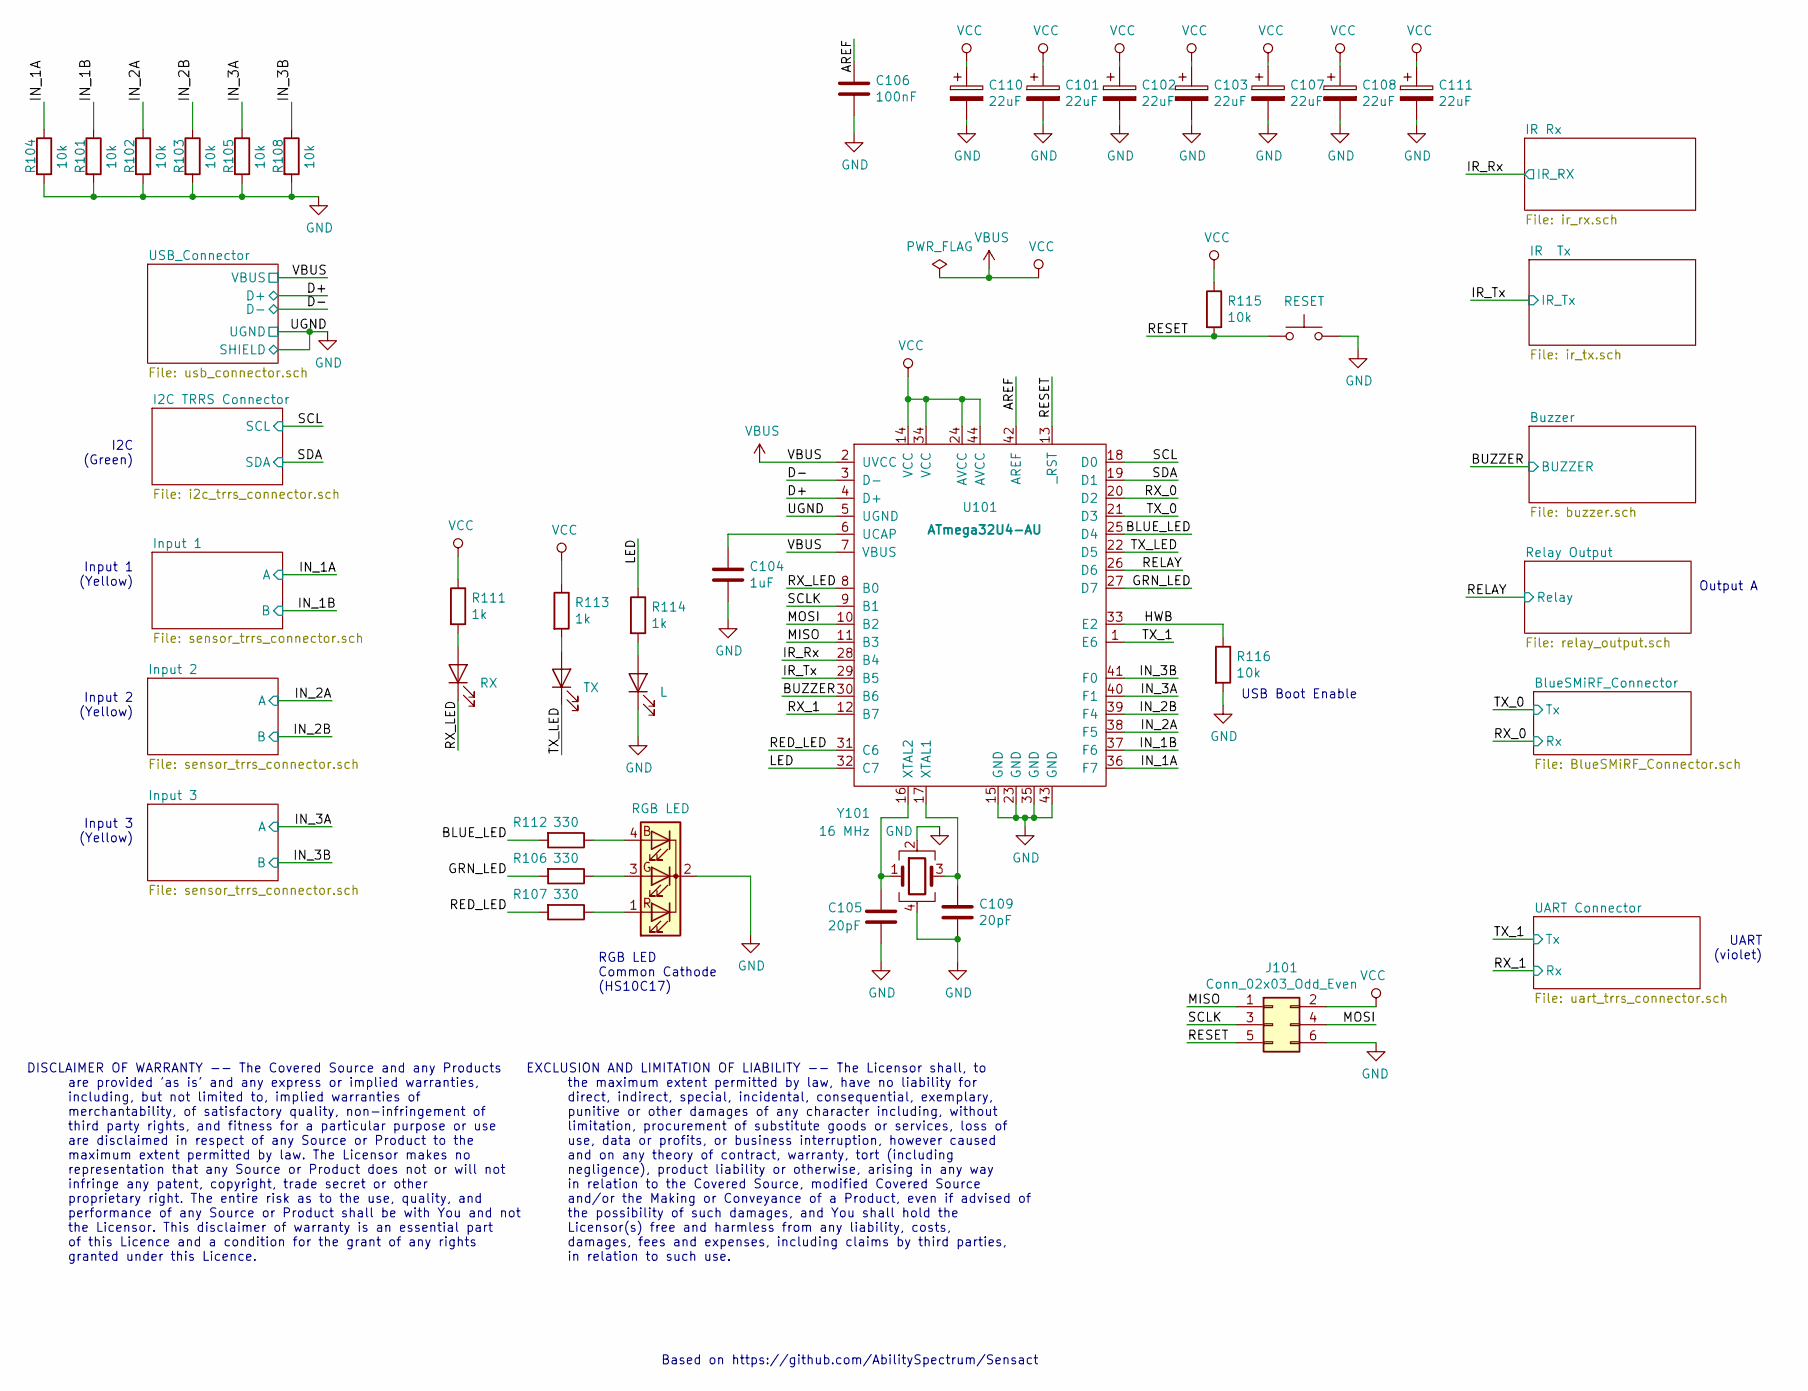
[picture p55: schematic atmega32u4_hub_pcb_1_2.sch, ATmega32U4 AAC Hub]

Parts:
C101, C102, C103, C107, C108, C110, C111: 22uF; C_0805_2012Metric; LCSC C45783
C104: 1uF; C_0805_2012Metric; LCSC C28323
C105, C109: 20pF; C_0603_1608Metric; LCSC C1648
C106: 100nF; C_0805_2012Metric; LCSC C49678
D101: RX; LED_0603_1608Metric; LCSC C72043
D102: RGB LED; LED_D5.0mm-4_RGB
D103: TX; LED_0603_1608Metric; LCSC C2286
D104: L; LED_0603_1608Metric; LCSC C72038
J101: Conn_02x03_Odd_Even; PinHeader_2x03_P2.54mm_Vertical
R101, R102, R103, R104, R105, R108, R115, R116: 10k; R_0603_1608Metric; LCSC C25804
R106, R107, R112: 330; R_0603_1608Metric; LCSC C23138
R111, R113, R114: 1k; R_0603_1608Metric; LCSC C21190
SW101: RESET; SW_PUSH_6mm
U101: ATmega32U4-AU; TQFP-44_10x10mm_P0.8mm; LCSC C44854
Y101: 16 MHz; Crystal_SMD_3225-4Pin_3.2x2.5mm; LCSC C13738

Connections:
/AREF: C106.1, U101.42 (AREF)
/BLUE_LED: R112.2, U101.25 (D4)
/BUZZER: U101.30 (B6); also elsewhere on the board
/D+: U101.4 (D+); also elsewhere on the board
/D-: U101.3 (D-); also elsewhere on the board
/GRN_LED: R106.2, U101.27 (D7)
/HWB: R116.1, U101.33 (E2)
/IN_3A: R105.1, U101.40 (F1); also elsewhere on the board
/IN_3B: R108.1, U101.41 (F0); also elsewhere on the board
/IR_Rx: U101.28 (B4); also elsewhere on the board
/IR_Tx: U101.29 (B5); also elsewhere on the board
/LED: R114.1, U101.32 (C7)
/MISO: J101.1, U101.11 (B3)
/MOSI: J101.4, U101.10 (B2)
/RED_LED: R107.2, U101.31 (C6)
/RELAY: U101.26 (D6); also elsewhere on the board
/RESET: J101.5, R115.2, SW101.1, U101.13 (_RST)
/RX_0: U101.20 (D2); also elsewhere on the board
/RX_1: U101.12 (B7); also elsewhere on the board
/RX_LED: D101.1 (K), U101.8 (B0)
/SCL: U101.18 (D0); also elsewhere on the board
/SCLK: J101.3, U101.9 (B1)
/SDA: U101.19 (D1); also elsewhere on the board
/TX_0: U101.21 (D3); also elsewhere on the board
/TX_1: U101.1 (E6); also elsewhere on the board
/TX_LED: D103.1 (K), U101.22 (D5)
GND: C101.2, C102.2, C103.2, C104.2, C105.2, C106.2, C107.2, C108.2, C109.2, C110.2, C111.2, D102.2 (K), D104.1 (K), J101.6, R101.2, R102.2, R103.2, R104.2, R105.2, R108.2, R116.2, SW101.2, U101.5 (UGND), U101.15 (GND), U101.23 (GND), U101.35 (GND), U101.43 (GND), Y101.2, Y101.4; also elsewhere on the board
unnamed: C104.1, U101.6 (UCAP)
unnamed: C105.1, U101.16 (XTAL2), Y101.1
unnamed: C109.1, U101.17 (XTAL1), Y101.3
unnamed: D101.2 (A), R111.2
unnamed: D102.1 (RA), R107.1
unnamed: D102.3 (GA), R106.1
unnamed: D102.4 (BA), R112.1
unnamed: D103.2 (A), R113.2
unnamed: D104.2 (A), R114.2
VBUS: C101.1, C102.1, C103.1, C107.1, C108.1, C110.1, C111.1, J101.2, R111.1, R113.1, R115.1, U101.2 (UVCC), U101.7 (VBUS), U101.14 (VCC), U101.24 (AVCC), U101.34 (VCC), U101.44 (AVCC); also elsewhere on the board

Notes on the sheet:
Input 1 (Yellow)
I2C (Green)
Input 2 (Yellow)
Input 3 (Yellow)
Output A
USB Boot Enable
RGB LED Common Cathode (HS10C17)
Based on https://github.com/AbilitySpectrum/Sensact
UART (violet)
DISCLAIMER OF WARRANTY -- The Covered Source and any Products are provided 'as is' and any express or implied warranties, including, but not limited to, implied warranties of merchantability, of satisfactory quality, non-infringement of third party rights, and fitness for a particular purpose or us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
EXCLUSION AND LIMITATION OF LIABILITY -- The Licensor shall, to the maximum extent permitted by law, have no liability for direct, indirect, special, incidental, consequential, exemplary, punitive or other damages of any character including, without limitation, procurement of substitute goods or se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

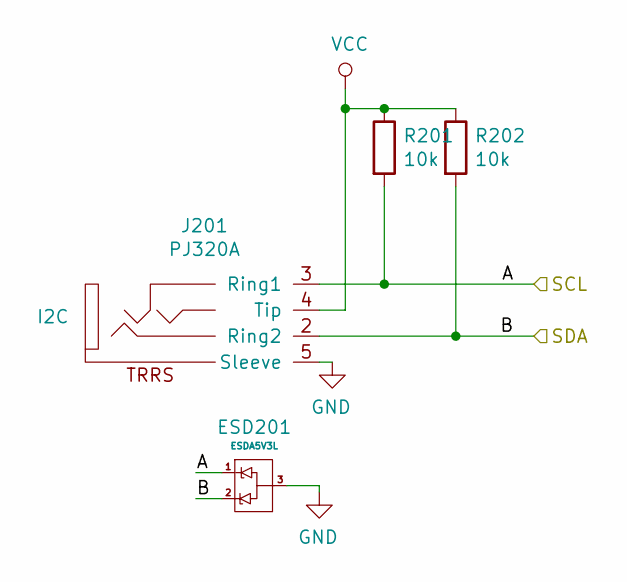
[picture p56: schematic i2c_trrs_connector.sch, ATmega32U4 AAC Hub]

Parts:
ESD201: ESDA5V3L; SOT-23; LCSC C87911
J201: PJ320A; PJ-320A
R201, R202: 10k; R_0603_1608Metric; LCSC C25804

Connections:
/SCL: ESD201.1, J201.3 (Ring1), R201.2; also elsewhere on the board
/SDA: ESD201.2, J201.2 (Ring2), R202.2; also elsewhere on the board
GND: ESD201.3, J201.5 (Sleeve); also elsewhere on the board
VBUS: J201.4 (Tip), R201.1, R202.1; also elsewhere on the board

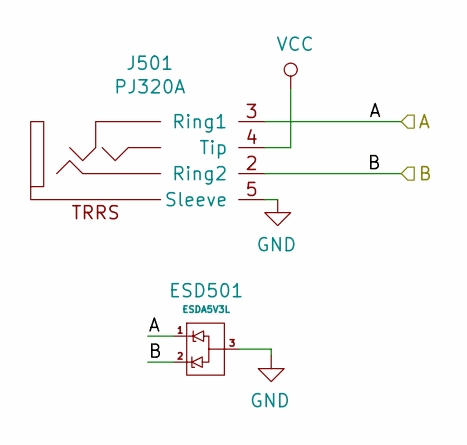
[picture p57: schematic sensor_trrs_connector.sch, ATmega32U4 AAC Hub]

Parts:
ESD401: ESDA5V3L; SOT-23; LCSC C87911
J301: PJ320A; PJ-320A

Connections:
GND: ESD401.3, J301.5 (Sleeve); also elsewhere on the board
VBUS: J301.4 (Tip); also elsewhere on the board

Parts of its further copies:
ESD301, ESD501: ESDA5V3L; SOT-23; LCSC C87911
J401, J501: PJ320A; PJ-320A

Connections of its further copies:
/IN_3A: ESD501.1, J501.3 (Ring1); also elsewhere on the board
/IN_3B: ESD501.2, J501.2 (Ring2); also elsewhere on the board
GND: ESD301.3, ESD501.3, J401.5 (Sleeve), J501.5 (Sleeve); also elsewhere on the board
VBUS: J401.4 (Tip), J501.4 (Tip); also elsewhere on the board

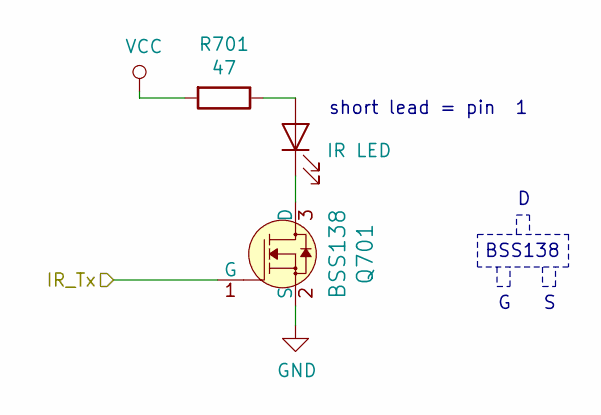
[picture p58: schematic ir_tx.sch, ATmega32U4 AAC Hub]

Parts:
D701: IR LED; LED_D5.0mm
Q701: BSS138; SOT-23; MPN BSS138; Digi-Key_PN BSS138CT-ND
R701: 47; R_1206_3216Metric; Part Number 1206W4J0470T5E; LCSC C25384

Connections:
/IR_Tx: Q701.1 (G); also elsewhere on the board
GND: Q701.2 (S); also elsewhere on the board
unnamed: D701.1 (K), Q701.3 (D)
unnamed: D701.2 (A), R701.1
VBUS: R701.2; also elsewhere on the board

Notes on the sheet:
BSS138
short lead = pin 1

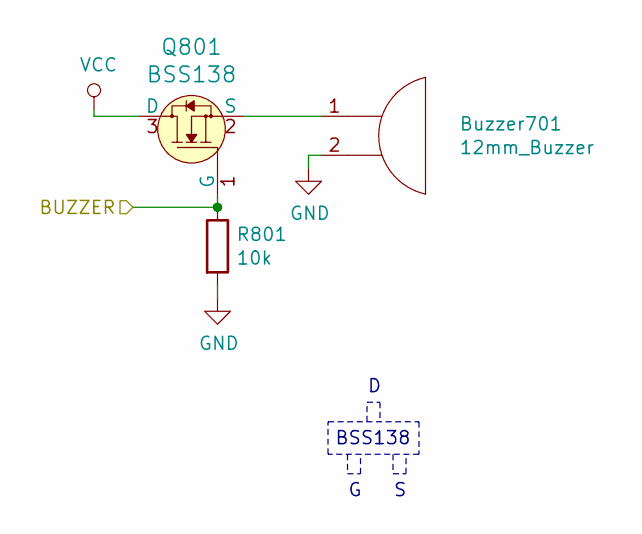
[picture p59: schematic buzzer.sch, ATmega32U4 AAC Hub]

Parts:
Buzzer701: 12mm_Buzzer; 12mm_buzzer
Q801: BSS138; SOT-23; MPN BSS138; Digi-Key_PN BSS138CT-ND
R801: 10k; R_0603_1608Metric; LCSC C25804

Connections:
/BUZZER: Q801.1 (G), R801.1; also elsewhere on the board
GND: Buzzer701.2, R801.2; also elsewhere on the board
unnamed: Buzzer701.1, Q801.2 (S)
VBUS: Q801.3 (D); also elsewhere on the board

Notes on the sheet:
BSS138

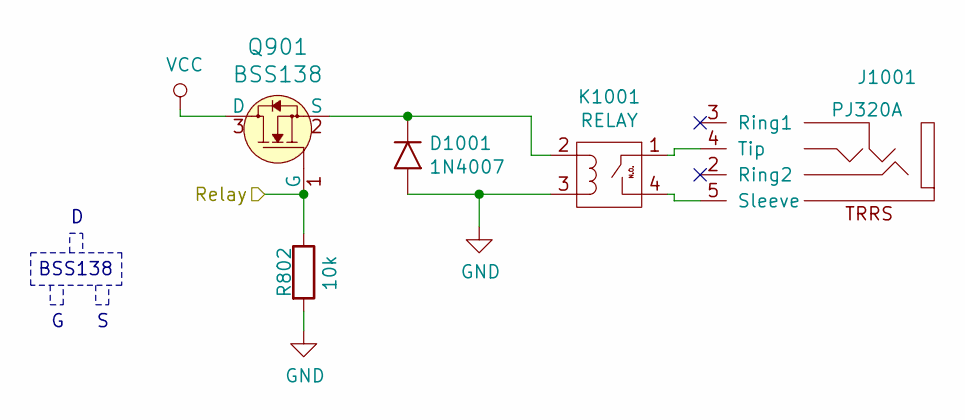
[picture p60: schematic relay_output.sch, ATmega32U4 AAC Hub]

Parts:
D901: 1N4007; D_SMA; LCSC C95872
J901: PJ320A; PJ-320A
K901: RELAY; sip-1a05
Q802: BSS138; SOT-23; MPN BSS138; Digi-Key_PN BSS138CT-ND
R802: 10k; R_0603_1608Metric; LCSC C25804

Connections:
/RELAY: R802.1; also elsewhere on the board
GND: R802.2; also elsewhere on the board

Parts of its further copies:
D1001: 1N4007; D_SMA; LCSC C95872
J1001: PJ320A; PJ-320A
K1001: RELAY; sip-1a05
Q901: BSS138; SOT-23; MPN BSS138; Digi-Key_PN BSS138CT-ND

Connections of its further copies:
/RELAY: Q901.1 (G); also elsewhere on the board
GND: D1001.2 (A), K1001.3; also elsewhere on the board
unnamed: D1001.1 (K), K1001.2, Q901.2 (S)
unnamed: J1001.4 (Tip), K1001.1
unnamed: J1001.5 (Sleeve), K1001.4
VBUS: Q901.3 (D); also elsewhere on the board

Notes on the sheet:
BSS138

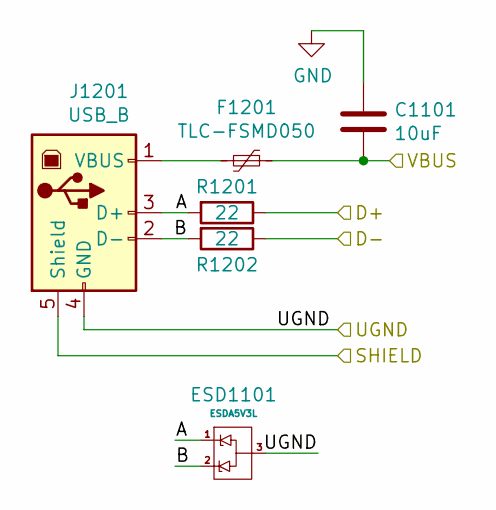
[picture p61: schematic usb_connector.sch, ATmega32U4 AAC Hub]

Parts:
C1101: 10uF; C_0805_2012Metric; LCSC C15850
ESD1101: ESDA5V3L; SOT-23; LCSC C87911
F1201: TLC-FSMD050; Fuse_0603_1608Metric; LCSC C261937
J1201: USB_B; USB_B_OST_USB-B1HSxx_Horizontal
R1201, R1202: 22; R_0603_1608Metric; LCSC C23345

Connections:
/D+: R1201.1; also elsewhere on the board
/D-: R1202.1; also elsewhere on the board
/USB_Connector/A: ESD1101.1, J1201.3 (D+), R1201.2
/USB_Connector/B: ESD1101.2, J1201.2 (D-), R1202.2
GND: C1101.1, ESD1101.3, J1201.4 (GND), J1201.5 (Shield); also elsewhere on the board
unnamed: F1201.2, J1201.1 (VBUS)
VBUS: C1101.2, F1201.1; also elsewhere on the board

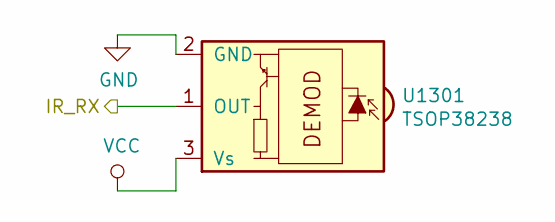
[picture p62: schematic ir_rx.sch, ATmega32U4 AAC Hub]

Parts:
U1301: TSOP38238; Vishay_MOLD-3Pin

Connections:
/IR_Rx: U1301.1 (OUT); also elsewhere on the board
GND: U1301.2 (GND); also elsewhere on the board
VBUS: U1301.3 (Vs); also elsewhere on the board

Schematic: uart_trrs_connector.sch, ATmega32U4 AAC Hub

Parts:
ESD1001: ESDA5V3L; SOT-23; LCSC C87911
J1101: PJ320A; PJ-320A

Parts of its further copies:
ESD1201: ESDA5V3L; SOT-23; LCSC C87911
J1202: PJ320A; PJ-320A

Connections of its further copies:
/RX_1: ESD1201.2, J1202.2 (Ring2); also elsewhere on the board
/TX_1: ESD1201.1, J1202.3 (Ring1); also elsewhere on the board
GND: ESD1201.3, J1202.5 (Sleeve); also elsewhere on the board
VBUS: J1202.4 (Tip); also elsewhere on the board

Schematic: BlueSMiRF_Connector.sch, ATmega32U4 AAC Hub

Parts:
ESD1202: ESDA5V3L; SOT-23; LCSC C87911
J1203: BlueSMiRF; BlueSMiRF_Socket

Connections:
/RX_0: ESD1202.2, J1203.3; also elsewhere on the board
/TX_0: ESD1202.1, J1203.2; also elsewhere on the board
GND: ESD1202.3, J1203.4; also elsewhere on the board
VBUS: J1203.5; also elsewhere on the board

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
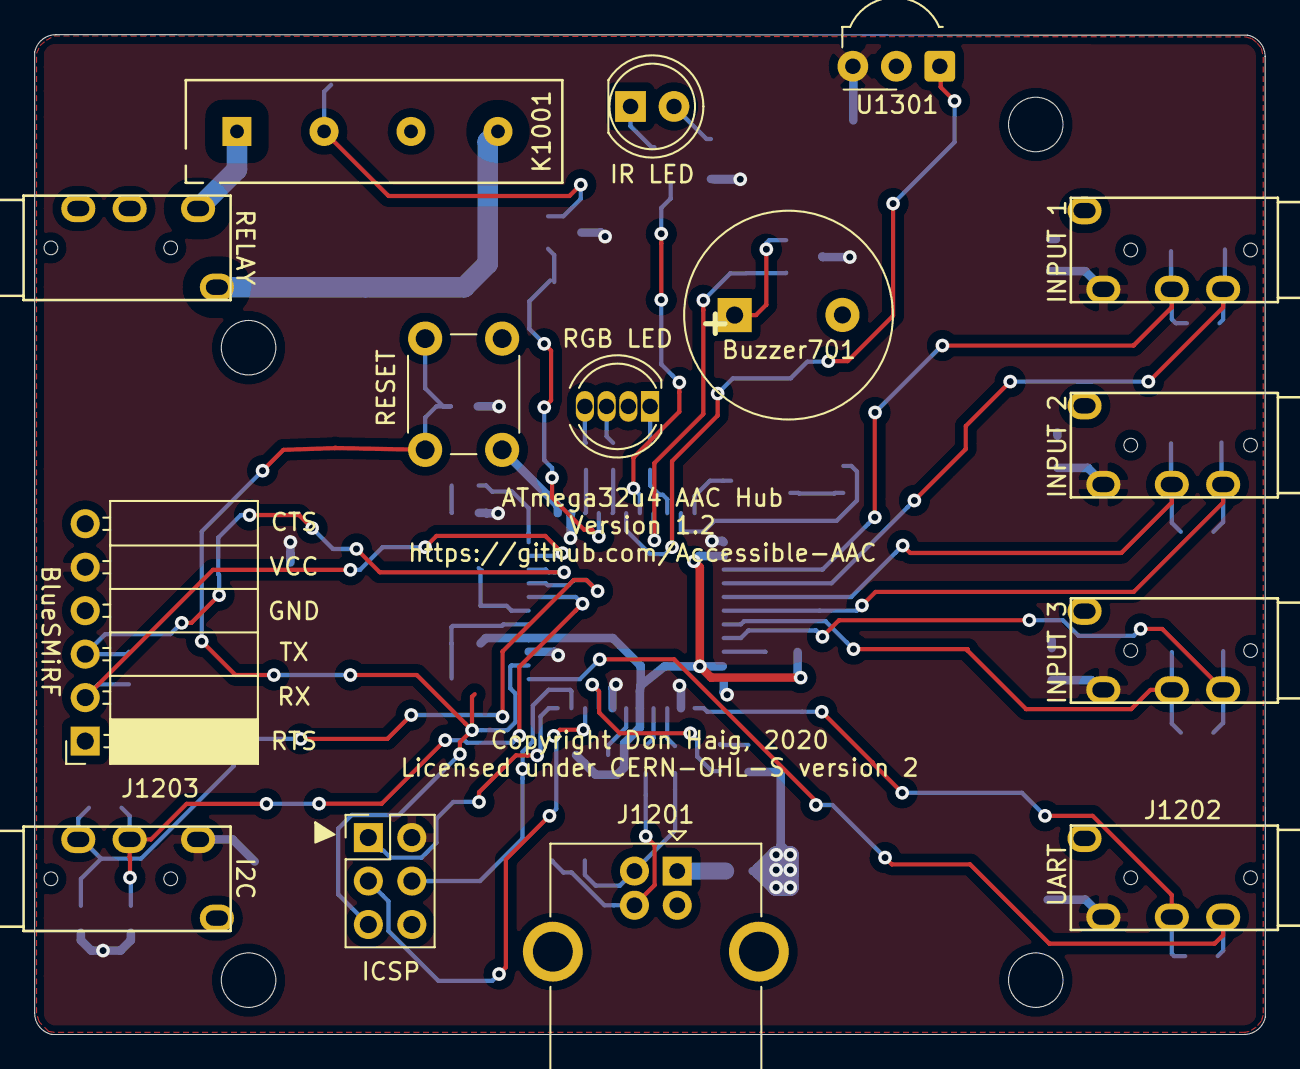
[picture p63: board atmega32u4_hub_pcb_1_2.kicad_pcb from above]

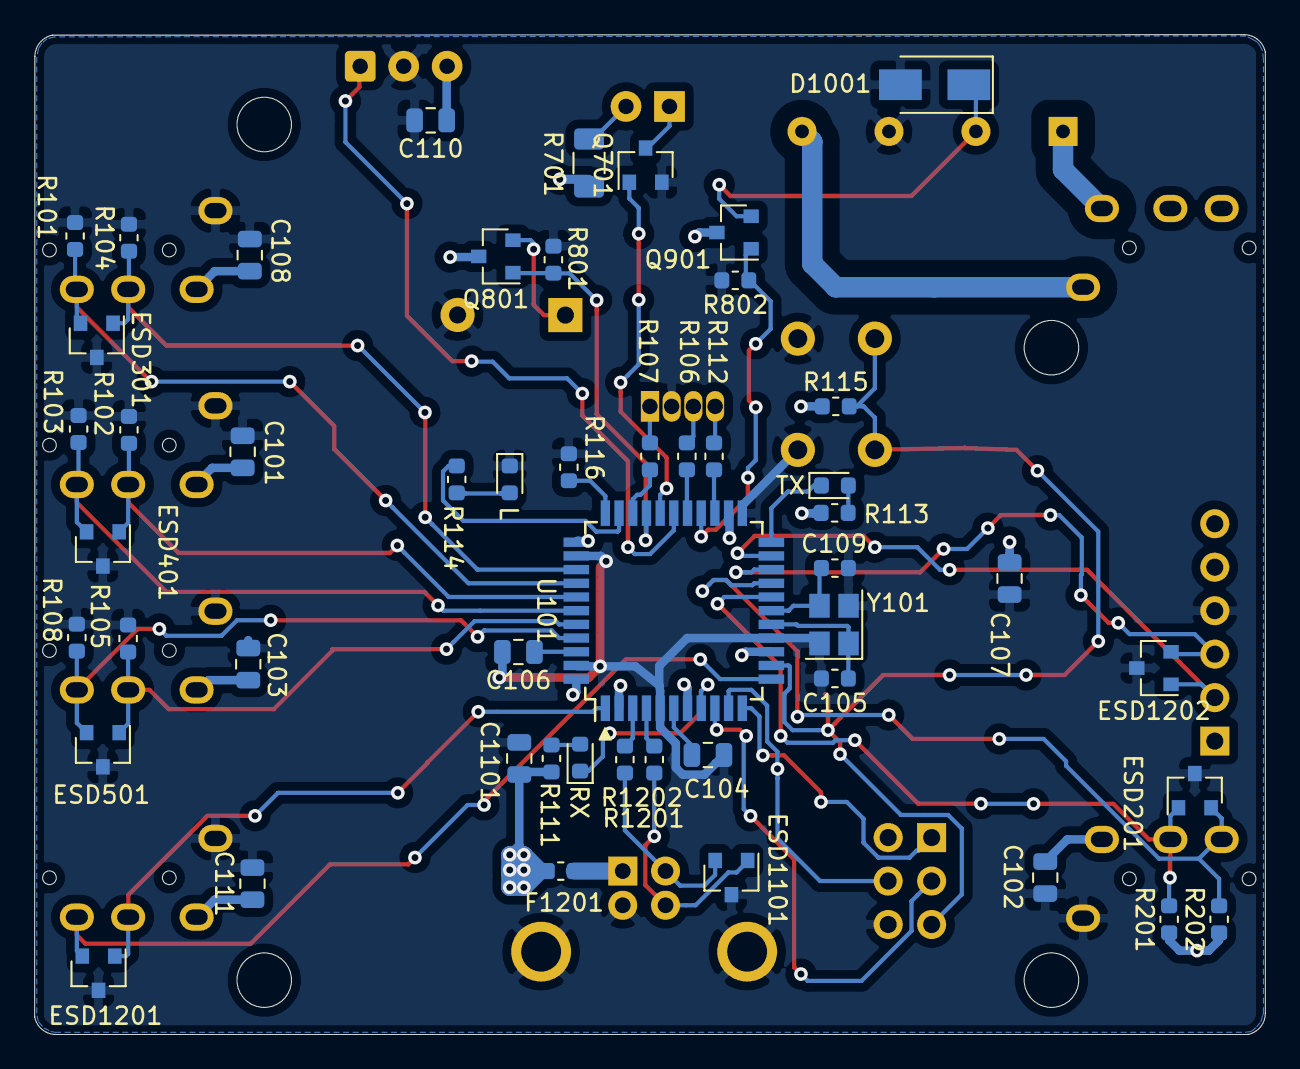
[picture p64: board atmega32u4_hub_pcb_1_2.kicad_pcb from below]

Board: 2 copper layers, 71.9 x 58.4 mm, 65 parts (50 on the bottom side), 50 nets.

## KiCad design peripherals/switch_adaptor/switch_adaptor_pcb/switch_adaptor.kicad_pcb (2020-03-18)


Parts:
J1, J2, J3: PJ320A; PJ-320A

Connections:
/SW1: J1.4 (Tip), J3.3 (Ring1)
/SW2: J2.4 (Tip), J3.2 (Ring2)
/Vcc: J1.2 (Ring2), J1.3 (Ring1), J1.5 (Sleeve), J2.2 (Ring2), J2.3 (Ring1), J2.5 (Sleeve), J3.4 (Tip)


Board: 2 copper layers, 25.1 x 23.4 mm, 3 parts (0 on the bottom side), 3 nets.

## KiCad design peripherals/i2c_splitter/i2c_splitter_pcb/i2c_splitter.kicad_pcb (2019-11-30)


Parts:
J1, J2, J3: PJ320A; PJ-320A

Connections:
/Gnd: J1.5 (Sleeve), J2.5 (Sleeve), J3.5 (Sleeve)
/SCL: J1.3 (Ring1), J2.3 (Ring1), J3.3 (Ring1)
/SDA: J1.2 (Ring2), J2.2 (Ring2), J3.2 (Ring2)
/V: J1.4 (Tip), J2.4 (Tip), J3.4 (Tip)


Board: 2 copper layers, 25.1 x 23.4 mm, 3 parts (0 on the bottom side), 4 nets.

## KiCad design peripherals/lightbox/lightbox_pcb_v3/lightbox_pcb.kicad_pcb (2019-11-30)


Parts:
D1, D2, D3, D4, D5, D6, D7, D8: LED; LED_D3.0mm
ESD1: PRTR5V0U2X; SOT-143
J1: PJ320A; PJ-320A
R1, R2, R3, R4, R5, R6, R7, R8: 220; R_Axial_DIN0207_L6.3mm_D2.5mm_P7.62mm_Horizontal
R9, R10: 10k; R_Axial_DIN0207_L6.3mm_D2.5mm_P7.62mm_Horizontal
U1: MCP23008-E_P; DIP-18_W7.62mm; MPN MCP23008-E/P; Digi-Key_PN MCP23008-E/P-ND

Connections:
+5V: ESD1.4 (V), J1.4 (Tip), R9.2, R10.2, U1.6 (~RESET), U1.18 (VDD)
/LED_0: R2.2, U1.10 (GP0)
/LED_1: R3.2, U1.11 (GP1)
/LED_2: R4.2, U1.12 (GP2)
/LED_3: R5.2, U1.13 (GP3)
/LED_4: R1.2, U1.14 (GP4)
/LED_5: R6.2, U1.15 (GP5)
/LED_6: R7.2, U1.16 (GP6)
/LED_7: R8.2, U1.17 (GP7)
/SCL: ESD1.2 (I/O_1), J1.3 (Ring1), R9.1, U1.1 (SCL)
/SDA: ESD1.3 (I/O_2), J1.2 (Ring2), R10.1, U1.2 (SDA)
GND: D1.1 (K), D2.1 (K), D3.1 (K), D4.1 (K), D5.1 (K), D6.1 (K), D7.1 (K), D8.1 (K), ESD1.1 (GND), J1.5 (Sleeve), U1.3 (A2), U1.4 (A1), U1.5 (A0), U1.9 (VSS)
unnamed: D1.2 (A), R1.1
unnamed: D2.2 (A), R2.1
unnamed: D3.2 (A), R3.1
unnamed: D4.2 (A), R4.1
unnamed: D5.2 (A), R5.1
unnamed: D6.2 (A), R6.1
unnamed: D7.2 (A), R7.1
unnamed: D8.2 (A), R8.1

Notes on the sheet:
GPIOs have 25 mA sink/source capabilty.
Rainbow ======= Yellow Blue Orange Red Yellow Blue Orange Red
Or use all white LEDs



Board: 2 copper layers, 26.4 x 108.0 mm, 23 parts (12 on the bottom side), 20 nets.

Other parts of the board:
1pin_prototyping, 1pin_prototyping#2: val**; 1pin_prototyping

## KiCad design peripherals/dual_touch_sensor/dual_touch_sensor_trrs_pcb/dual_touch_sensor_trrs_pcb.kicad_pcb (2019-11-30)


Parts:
J1: PJ320A; PJ-320A
S1, S2: catalex_touch_sensor; Catalex_Touch_Module

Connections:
+5V: J1.4 (Tip), S1.2 (Vcc), S2.2 (Vcc)
/Signal_1: J1.3 (Ring1), S1.3 (Sig)
/Signal_2: J1.2 (Ring2), S2.3 (Sig)
GND: J1.5 (Sleeve), S1.1 (Gnd), S2.1 (Gnd)

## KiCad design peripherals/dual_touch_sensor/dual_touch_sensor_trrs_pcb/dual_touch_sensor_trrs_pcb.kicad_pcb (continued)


Board: 2 copper layers, 43.9 x 13.0 mm, 3 parts (1 on the bottom side), 4 nets.

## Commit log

2019-11-26 Arduino Leonardo Controller Enclosure Design Files
    [enclosure.scad, enclosure_bottom_v2.stl, enclosure_top_v2.stl, pcbs.scad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]
2019-11-30 Peripheral Design Files
    [59mm_button.scad, 59mm_test.stl, 59mm_test2.stl, arcade_joystick_bottom.stl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]
2020-02-21 Extension rod for HW-504 joytick
    [hw-504_handle.stl, hw-504_stick.scad]
2020-02-21 Cleaned up code
    [hw-504_stick.scad]
2020-03-18 Updated arcade joystick pcb design
    [arcade_joystick_pcb-B_Cu.gbl, arcade_joystick_pcb-B_Mask.gbs, arcade_joystick_pcb-B_Paste.gbp, arcade_joystick_pcb-B_SilkS.gbo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]
2020-03-18 Updated switch adaptor design
    [switch_adaptor-B_Cu.gbl, switch_adaptor-B_Mask.gbs, switch_adaptor-B_SilkS.gbo, switch_adaptor-Edge_Cuts.gm1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]
2020-07-12 Increased tactile switch PCB hole diameters - increased hole diameters to 1.2mm to accommodate pins on 12mm x 12mm tactile switches.
    [tactile_switch_pcb_v2-B_Cu.gbl, tactile_switch_pcb_v2-B_Mask.gbs, tactile_switch_pcb_v2-B_Paste.gbp, tactile_switch_pcb_v2-B_SilkS.gbo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]
2020-09-16 Refactored palm rest design
    [captive_nut.scad, palm_rest.scad, palm_rest.stl, palm_rest_v2.scad]
2020-11-06 Added missing openscad straight header model
    [straight_header.scad]
2021-11-09 Update README.md
    https://forum.kicad.info/t/warning-avoid-all-links-to-kicad-pcb-org-use-kicad-org/31521
2021-12-17 AtMega32U04 controller designs added
    [BlueSMiRF_Connector.sch, arcade_joystick_pcb.kicad_pcb, arcade_joystick_pcb.sch, atmega32u4_cpu.sch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]

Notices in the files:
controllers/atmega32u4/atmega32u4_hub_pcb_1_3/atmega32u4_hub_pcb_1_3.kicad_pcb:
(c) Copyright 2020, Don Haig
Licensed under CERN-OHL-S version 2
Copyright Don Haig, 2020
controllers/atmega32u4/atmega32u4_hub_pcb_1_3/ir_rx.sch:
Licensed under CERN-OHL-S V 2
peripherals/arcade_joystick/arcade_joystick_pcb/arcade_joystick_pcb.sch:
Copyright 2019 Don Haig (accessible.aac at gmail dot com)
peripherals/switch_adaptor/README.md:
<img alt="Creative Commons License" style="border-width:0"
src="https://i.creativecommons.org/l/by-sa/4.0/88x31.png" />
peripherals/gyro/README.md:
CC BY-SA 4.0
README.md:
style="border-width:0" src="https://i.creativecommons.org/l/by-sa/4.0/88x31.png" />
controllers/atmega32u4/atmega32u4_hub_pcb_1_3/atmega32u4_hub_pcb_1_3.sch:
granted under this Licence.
